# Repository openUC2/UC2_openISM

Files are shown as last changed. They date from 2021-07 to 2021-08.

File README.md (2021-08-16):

<p align="left">

</p>

# openUC2 openISM
---

This is the repository for the openISM project which integrates a laser-scanning module for image-scanning microscopy (ISM) to the UC2-system.

🧾 The manuscript for the openISM and openSIM can be found under the [DOI:10.1101/2021.01.08.425840](https://doi.org/10.1101/2021.01.08.425840)

<p align="center">
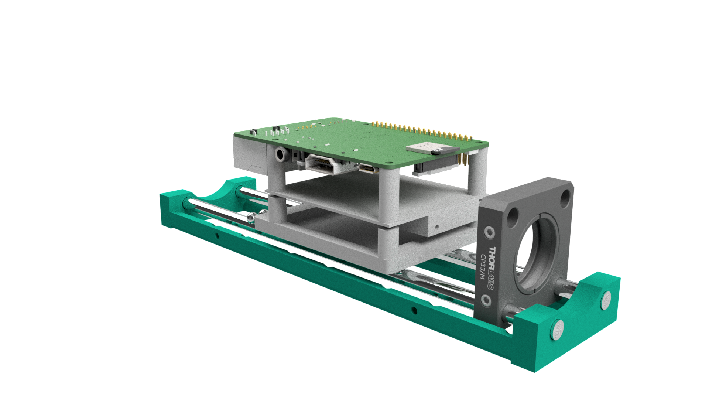
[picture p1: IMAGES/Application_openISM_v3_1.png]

</p>

***Fig 1:*** *This is the ready-to-print module which clicks into the UC2-system. It hosts the Nebra AnyBeam HAT with a Raspberry Pi as a control unit*

This module is based on the work about Image Scanning Microscopy (ISM) by Enderlein et al. [1] and instant Structured Illumination Microscopy (iSIM) by A. York et al. [2]. It uses a low-cost MEMS-based laser-scanning video-project ([Sony CL1A, Tokyo, Japan, 300€](https://www.sony.com.sg/electronics/support/televisions-projectors-projectors/mp-cl1a/specifications); [Anybeam HAT, UK, 200€](https://uk.pi-supply.com/products/nebra-anybeam-hat-laser-projector-for-the-raspberry-pi?lang=de)) to generate a structured illumination for microscopy. We apply a point-wise incoherent lattice/grid-like pattern to increase lateral and axial resolution. The overall gain in resolution is limited, hence more suitable for educational purposes or data generation.  

<p align="center">
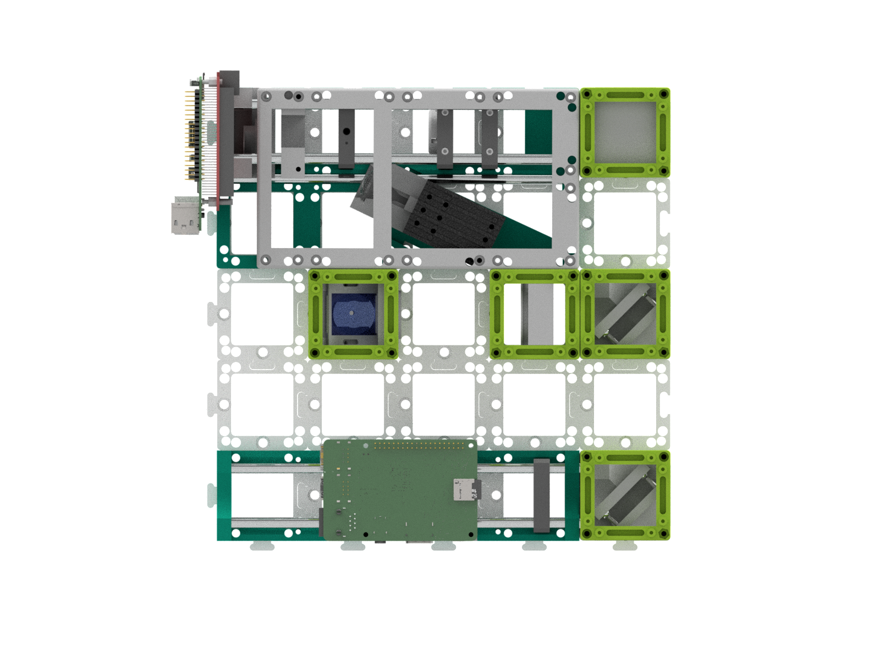
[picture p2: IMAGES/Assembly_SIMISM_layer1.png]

</p>

***Fig 2:*** *This shows the optical assemlby; the laser beam deflected by the scanning mirror is "collimated" and stired by a set of two kinematic mirror mounts before a tube lens (f'=165mm) forms a magnified image in back focal plane (BFP) of the objective lens (not shown) which follows the dichroic mirror*

In recent years portable devices to experience entertainment "on-the-go" like video-projectors or movie screens have found their ways to the consumer market. Many of these produce like portable projectors share the same components as their scientific counterparts (e.g. digital mirror devices, DMD) but for a much lower price since components are mass-produced. Besides wide-field projection system based on LCoS (liquid crystal on silica), LCD or DMD displays, more exotic laser-scanning based systems like the here used Sony MP.CL1A (Japan) enable the creation of laser-scanning microscopes for a very low price (e.g. 300€).

To display a color image on a screen (e.g. wall), a small MEMS (Micro-Electro-Mechanical Systems) scans a set of RGB Blue=450nm, Green}=530, Red = 650, laser-beams over the 2D (e.g. X/Y) plane with a frame-rate of 60fps at a spatial resolution of 1920*720 pixel^2.
This device can easily be integrated in the UC2-system by providing a customized  adapter which makes the device compatible with the 50*5 mm^2 grid. Following the work by Enderlein et al. (ISM) (Muller2010a) and York et al. (iSIM)  (York2012) we displayed an incoherent grid of point sources in the sample plane, which can be used to create a better optical sectioning and improve optical resolution. This is done in a post-processing step, where each 2D image gets divided in a series of tiles of the size of the PSF-extend around one illumination position. Each tile corresponds to a confocal-like measurement, where the information can computationally be confined, when a de-centred detection pinhole is assumed. The resulting signal is placed on a canvas with twice the sampling of the original measurement, which creates an optical super-resolution up to a factor of sqrt(2) (McGregor2015).

Since this device is not meant to be used for scientific instrumentation, there are only limited information available. Also, since the resolution of 1920*720 pixels^2 is not very common, ordinary computers to generate a display on this device where interpolating the images. Connecting the device to a Apple Macbook (USA) at a display-resolution of 720p ensured a one-to-one pixel mapping, where we created a customized Python-script to generate and display the ISM-patterns full-screen. The monochromatic cellphone-camera (Huasei P20, China) was driven using the open-source software FreeDCam (Fuchs2018), where the exposure time t=1/60s matches the frame-rate of the laser-scanning projector in order to reduce bouncing effects of both refresh-rates.

<p align="center">
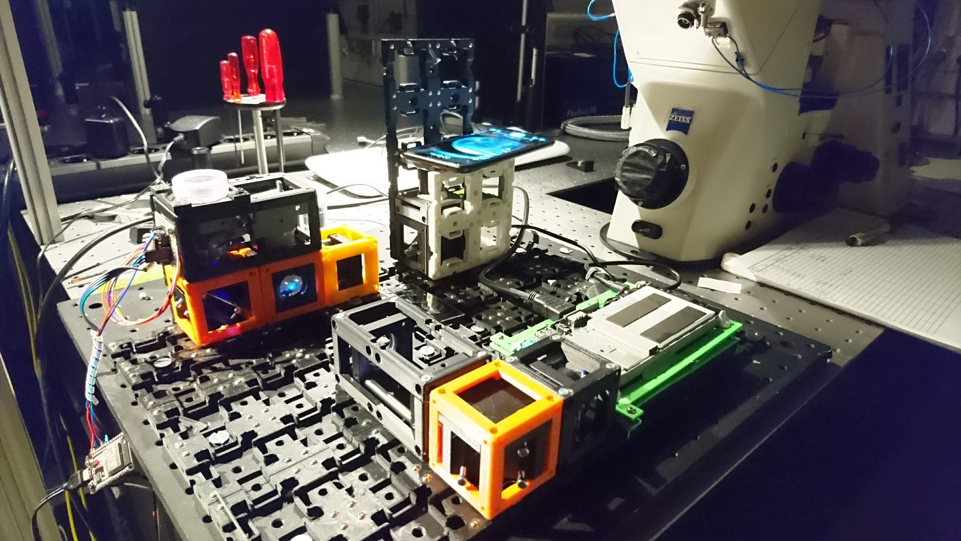
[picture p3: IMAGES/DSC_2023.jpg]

</p>

***Fig 3:*** *The full system based on the modular cubes. This variant is based on a cellphone camera as the detection system. Also instead of the AnyBeam MEMS projector, we use the SONY device*

***Features:***
- Increased optical sectioning and higher resolution
- Very low cost:  ~300€
- Easy to align
- Open-Source
- Three wavelengths

## Optical System

<p align="center">
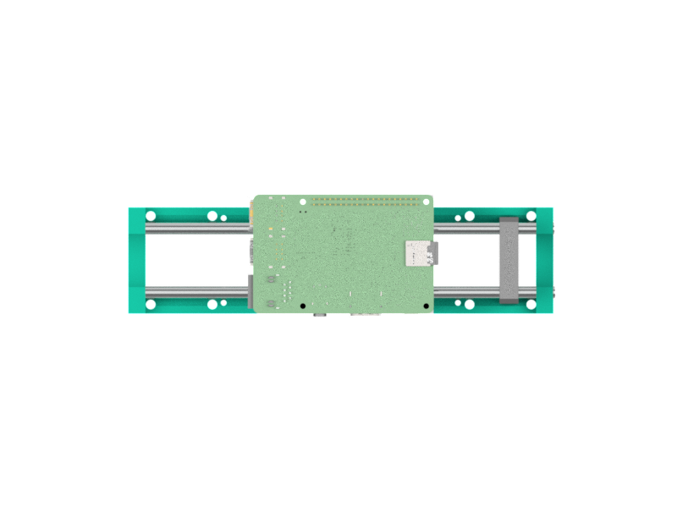
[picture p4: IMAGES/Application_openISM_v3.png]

</p>

## Optical Setup

**NEED TO BE UPDATED**

The optical setup shown in Fig. 1 is straight-forward. The resonating MEMS in the projector needs to be imaged into the BFP of the microscope objective lens. In order to get high-resolution images, the BFP is over-filled by the mirror ideally. We assumed a diameter of the aluminium mirror of d_{mirror}=1.5mm and a diameter of the BFP of around d_{BFP}=5.5mm which requires a telescope, created by a lens f'_1=30mm and a following tube-lens f'_2=180mm. The low-cost infinity-corrected microscope objective (Optika, 20x, NA=0.4,  N-plan, [here](https://www.optik-pro.de/fuer-mikroskope/optika-objektiv-20x-0-40-infinity-n-plan-pol-b-383pol-m-146p/p,56893#tab_bar_1_select) was put in a motor-driven Z-stage to allow focussing the objective relative to the sample. A set of different dichroic-mirror cubes with suitable filters allows the switching between different fluorophores and excitation wave-lengths.

# Table of Content
* **[Software](#-software)**
* **[Hardware](#-hardware)**
* **[Bill of materials](#-bill-of-materials)**
* **[Electronics](#-electronics)**
* **[Results](#-results)**

# Software
### Install the Anybeam Nebra with the Raspberry Pi

Please follow the steps mentioned on the [AnyBeam HAT github page](https://github.com/NebraLtd/AnyBeam/).

Open the file ```/boot/config.txt``` and add the following lines:

```
# Additional overlays and parameters are documented /boot/overlays/README
dtoverlay=dpi24
overscan_left=0
overscan_right=0
overscan_top=0
overscan_bottom=0
framebuffer_width=1280
framebuffer_height=720
enable_dpi_lcd=1
display_default_lcd=1
dpi_group=2
dpi_mode=85
dpi_output_format=0x070027
```

# Hardware

Below we describe how the device can be build and assembled in order to replicate the whole system as shown in the rendering above. One needs additional parts that can be found in the core [openUC2 repository](https://github.com/bionanoimaging/UC2-GIT).

## Electronics
### Having a look into the MEMS-based laser projector (old version with Sony)

<p align="center">
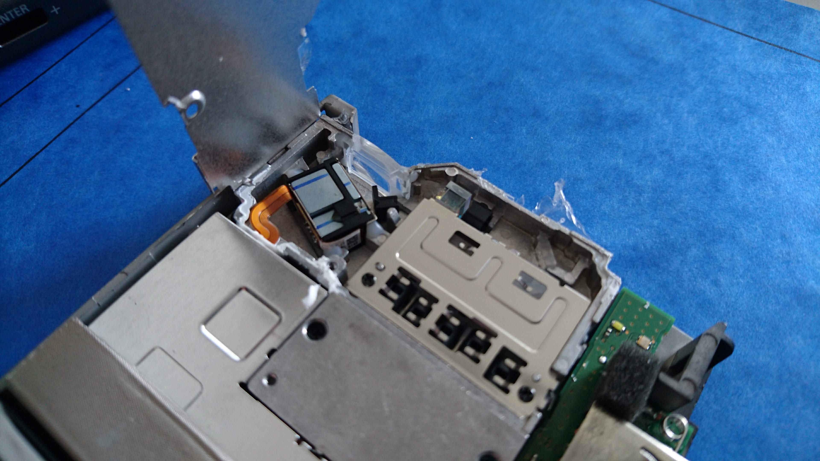
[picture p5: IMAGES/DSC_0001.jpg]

</p>

***Fig 1:*** *The assembly faeatures three laser wavelengths fused with a complicated assembly of optical parts to remove speckles*

<p align="center">
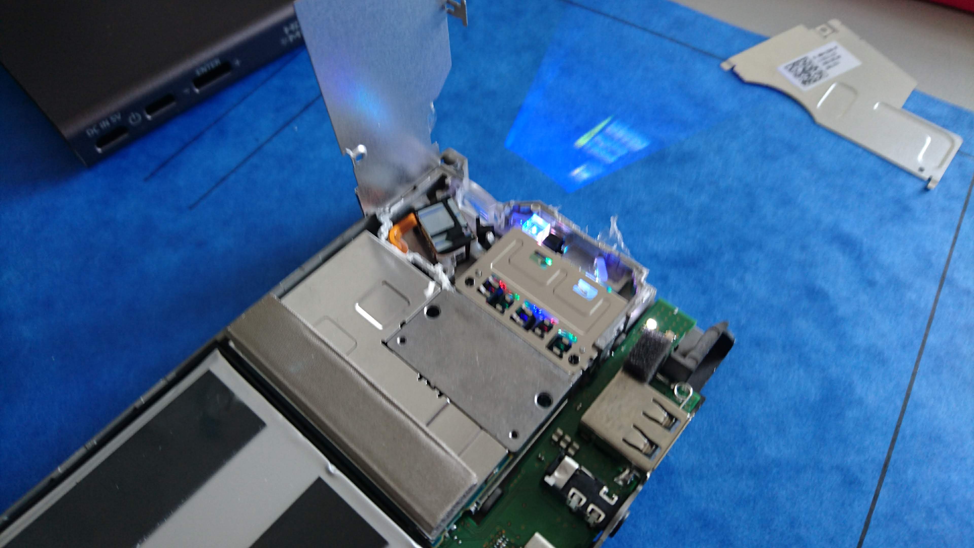
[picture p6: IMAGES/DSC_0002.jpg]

</p>

***Fig 2:*** *Funnily, the polarization beamsplitter from a bluray drive fits in there to enable any kind of descanning arrangement*

<p align="center">
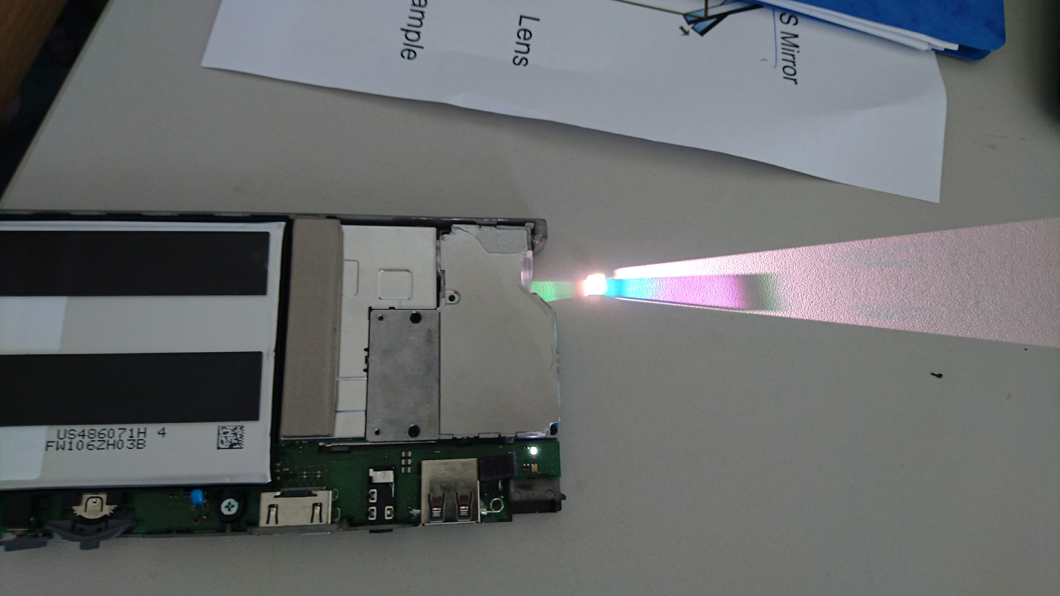
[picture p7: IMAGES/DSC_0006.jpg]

</p>

***Fig 3:*** *Beam coming out of the projector*

## Bill of material

Below you will find all components necessary to build this device

### 3D printing files

All these files need to be printed. We used a Prusa i3 MK3 using PLA Prusament (Galaxy Black) at layer height x.x mm and infill xx%.

Parts to print:

* 1× [openISM AnyBeam Mount](./CAD/20_Cube_insert_openISM_AnyBeamMount.stl)
* 1× [Cube insert openISM vase v3](./CAD/20_Cube_insert_openISM_vase_v3.stl)

### Additional parts
This is used in the current version of the setup

<strong>(This is for the Anybeam, since the Sony projector seems to be discontinued)</strong>

|  Type | Details  |  Price | Link  |
|---|---|---|---|
| MEMS | Nebra AnyBeam HAT |  200 € | [Pi Supply](https://uk.pi-supply.com/products/nebra-anybeam-hat-laser-projector-for-the-raspberry-pi?lang=de)  |
| Raspberry Pi | Raspi+SD-Card+Case+Powersupply(for DMD+Raspi, 5V, >=3A!) |  70 € | [Reichelt](https://www.reichelt.de/raspberry-pi-4-b-4x-1-5-ghz-1-gb-ram-wlan-bt-rasp-pi-4-b-1gb-p259874.html?PROVID=2788&gclid=Cj0KCQiAz53vBRCpARIsAPPsz8X9hCOt9yVVB_WqLCmKSs2e-KuThVnrMEtl2TRbAUTqtVoNZU3zM3YaAg2ZEALw_wcB&&r=1)  |
| "Scan" lens | 1x Achromatic 1 inch Lens, f=30mm |  82 € | [Thorlabs](https://www.thorlabs.com/thorproduct.cfm?partnumber=AC254-030-A)  |
| 5mm ball magnets  | 8x Neodym Ball Magnets |  5 € | [Various]()  |
| 6mm Rods | 20mm Rods (ferromagnetic/galvanized), 6mm diameter   |  40 € | [Thorlabs, Edmund Optics ?]()  |
| M3 Screws | Various |  1 € | [Various]()  |

### Design files
The original design files are in the [INVENTOR](./INVENTOR) folder. *FOR ANOTHER FORMAT, GET YOUR OWN FOLDER.*

### Problems with the Nebra Anybeam

The pattern of the Nebra Anybeam HAT seems to fluctuate temporally. We believe this is due to the scanning scheme of the MEMS.
Read more [here](https://github.com/NebraLtd/AnyBeam/issues/14).

<p align="center">

</p>

***Fig 1:*** *One can observe a gitter which moves temporally*

<p align="center">

</p>

***Fig 2:*** *The three different wavelenghts are not in-line*

<p align="center">
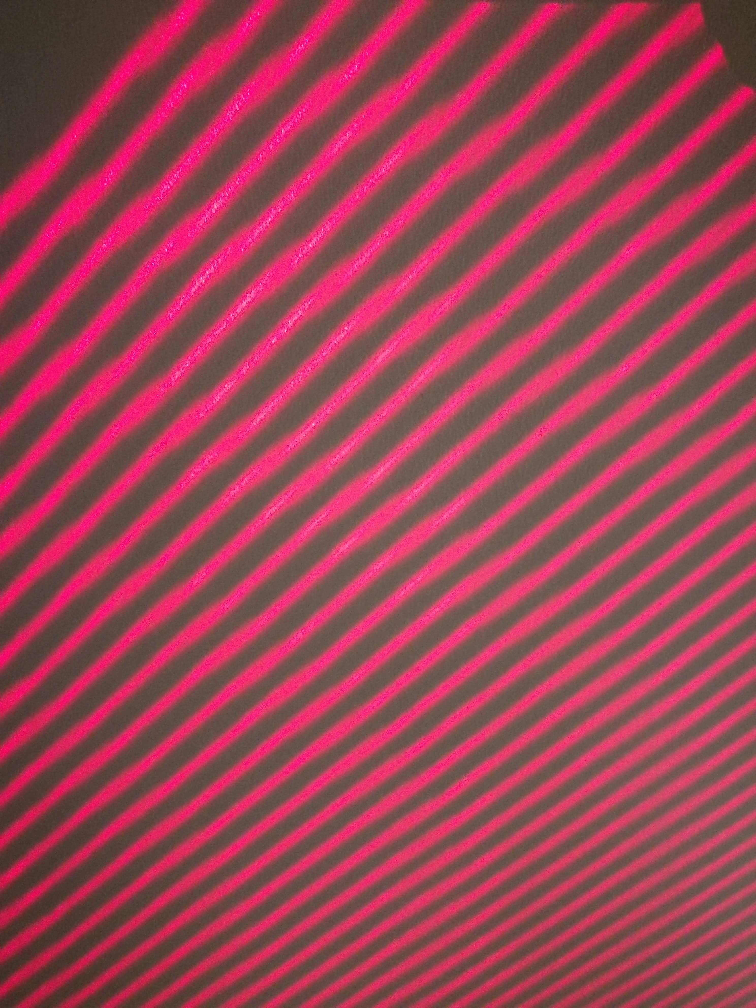
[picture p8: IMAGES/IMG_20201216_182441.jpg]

</p>

***Fig 3:*** *Inhomogenities due to bouncning of the pixels*

## Showcase
This is just one frame of some fluorescent pollen grains:
<p align="center">
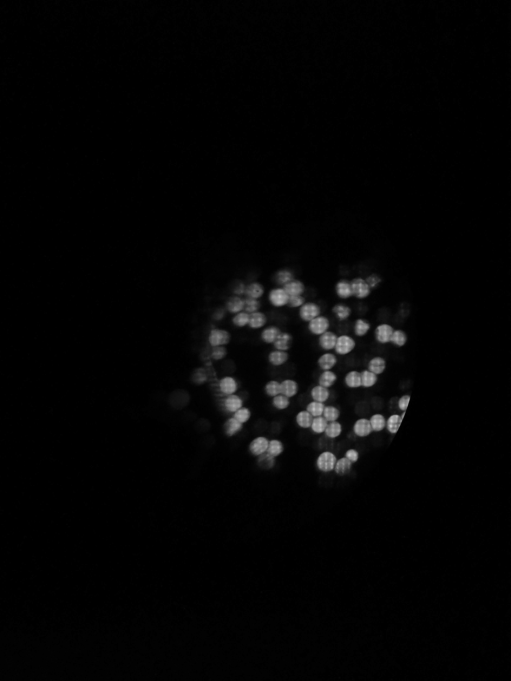
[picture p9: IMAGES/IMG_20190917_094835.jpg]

</p>

<p align="center">
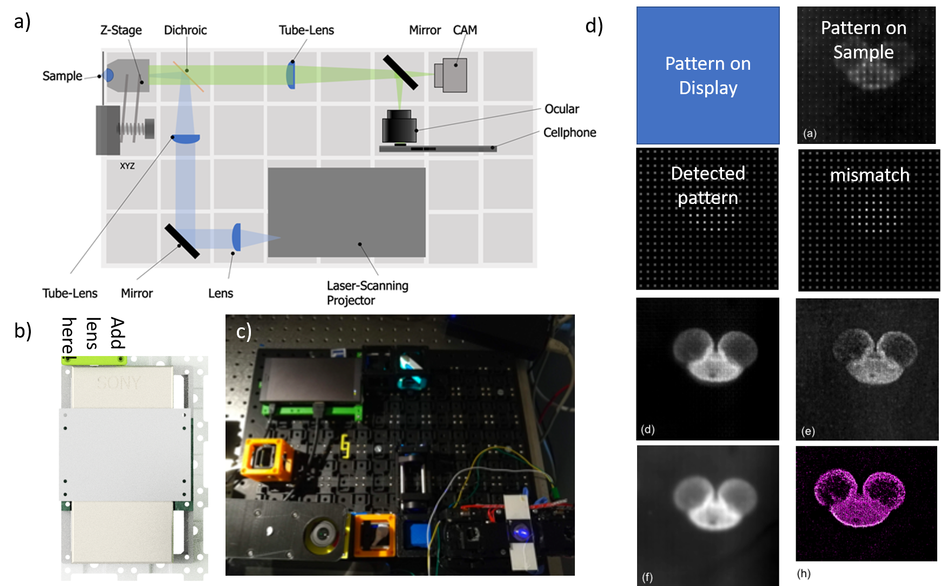
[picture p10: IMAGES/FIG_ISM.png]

</p>

## Get Involved

This project is open so that anyone can get involved. You don't even have to learn CAD designing or programming. Find ways you can contribute in  [CONTRIBUTING](https://github.com/openUC2/UC2-GIT/blob/master/CONTRIBUTING.md)

## License and Collaboration

This project is open-source and is released under the CERN open hardware license. Our aim is to make the kits commercially available.
We encourage everyone who is using our Toolbox to share their results and ideas, so that the Toolbox keeps improving. It should serve as a easy-to-use and easy-to-access general purpose building block solution for the area of STEAM education. All the design files are generally for free, but we would like to hear from you how is it going.

You're free to fork the project and enhance it. If you have any suggestions to improve it or add any additional functions make a pull-request or file an issue.

Please find the type of licenses [here](https://github.com/openUC2/UC2-GIT/blob/master/License.md)

REMARK: All files have been designed using Autodesk Inventor 2019 (EDUCATION)

## Collaborating
If you find this project useful, please like this repository, follow us on Twitter and cite the webpage! :-)

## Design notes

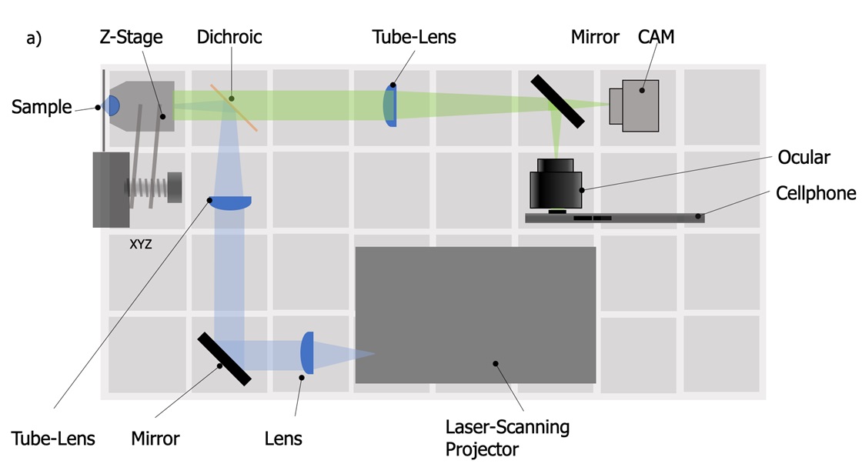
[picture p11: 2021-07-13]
IMAGES/ISM.jpg

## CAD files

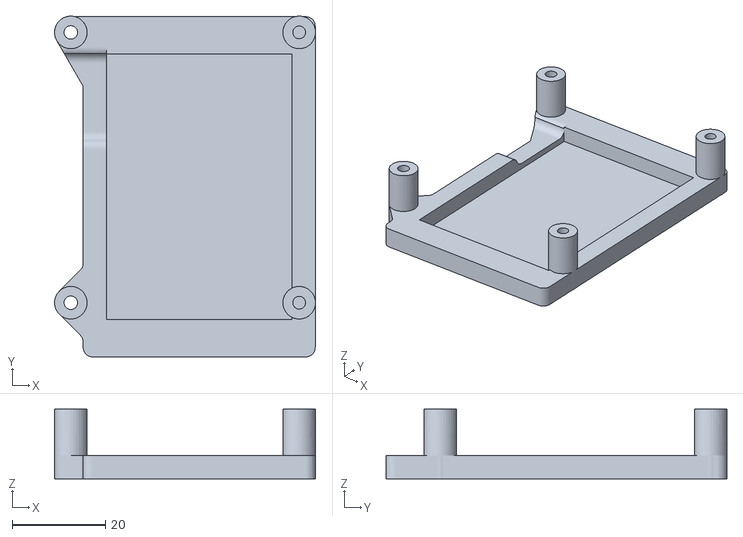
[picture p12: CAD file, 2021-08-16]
CAD/20_Cube_insert_openISM_AnyBeamMount.stl
56.0 x 73.1 x 15.0

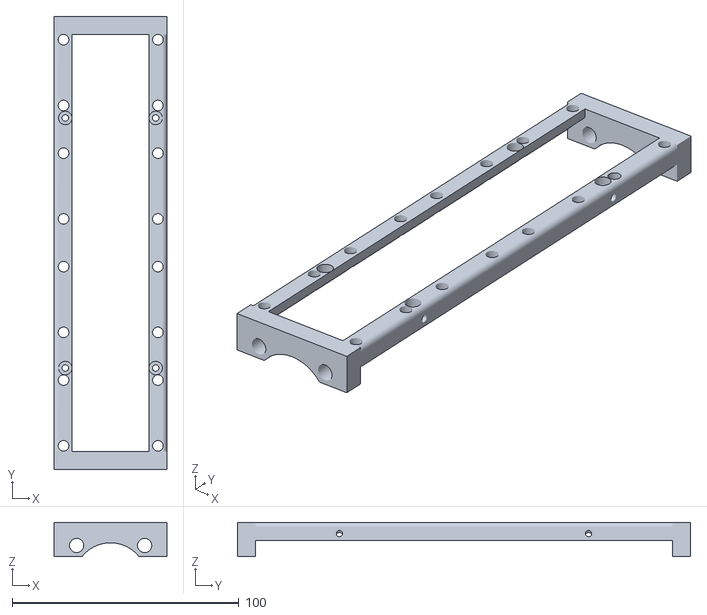
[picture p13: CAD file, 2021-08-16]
CAD/20_Cube_insert_openISM_vase_v3.stl
49.8 x 199.8 x 15.0

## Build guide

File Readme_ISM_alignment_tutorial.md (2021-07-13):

# ISM alignment tutorial

This tutorial is aming to align the openISM module to the microscope. The required components and setup steps are similar to the openSIM module which is in the Github repository.

  - openISM module
  - optical components
  - UC2 cubes and inserts
  - target sample
  - magical hand
  
## Introduction of the openISM module

In the openISM module, the illumination source is a commercially available laser video projector (Sony/Anybeam HAT). Both of them have integrated different colored laser diodes and the desired image is displayed with the help of a MEMS mirror. In this project, we have built a openSIM/ISM setup, which the imaging and sample modules of the setup are shared. The illumination of the openISM module is shown in Fig. 1. 
<p align="center">
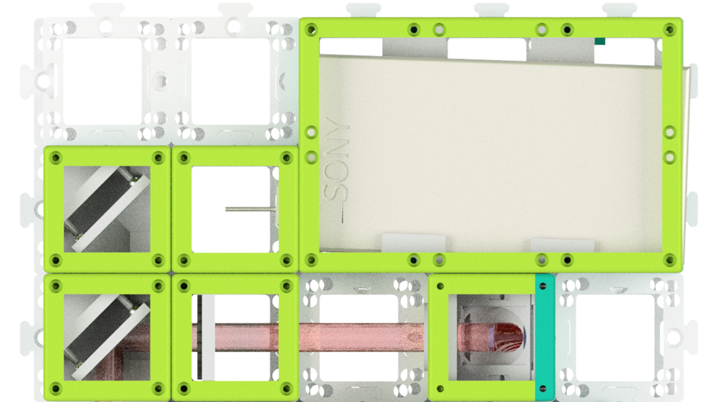
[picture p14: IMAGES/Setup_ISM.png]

</p>

***Fig. 1*** *The openISM illumination module based on our UC2 CAD design. Comparing to the openSIM module, the ISM part is relative simply thanks to the projector, which has integrated laser diodes and MEMS mirror. The laser beam is directed twice with the help of two mirrors and focus on the back focal plane of the objective.*

The spectra of both projectors are illustrated in Fig. 2
<p align="center">
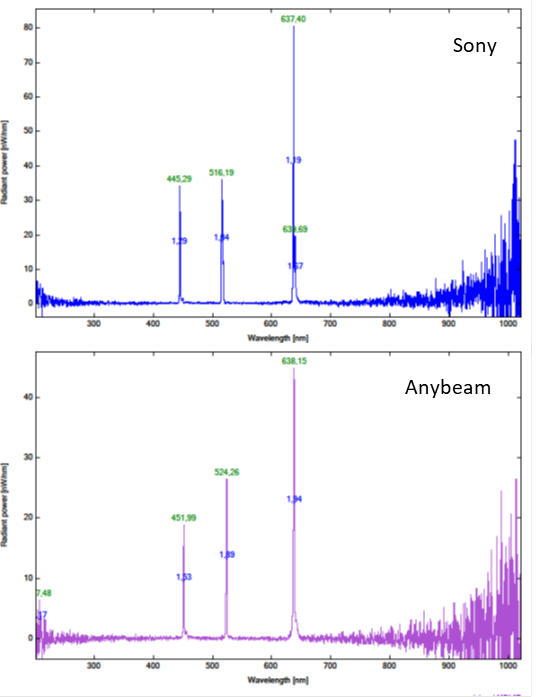
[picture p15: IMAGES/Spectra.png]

</p>

***Fig. 2*** *Spectra of Sony/Anybeam laser projector.Both projectors used the laser diodes which have similar spectra. They can used to excite fluorescent, such as GFP, mCherry and Alexa Flour 647, with the correct filter set.*

## Alignmen of the telescope
After collimate the beam with first lens, the beam is directed by two mirrors to the second 165 mm lens. After the second lens, the beam should refocus at the back focal plane (BFP) of the objective and reimage the MEMS mirror. Due to the effct of the freeform lens integrated in the sony projector, the collimated beam from sony shaped a round shape with some unexpected external strucutres.

<p align="center">
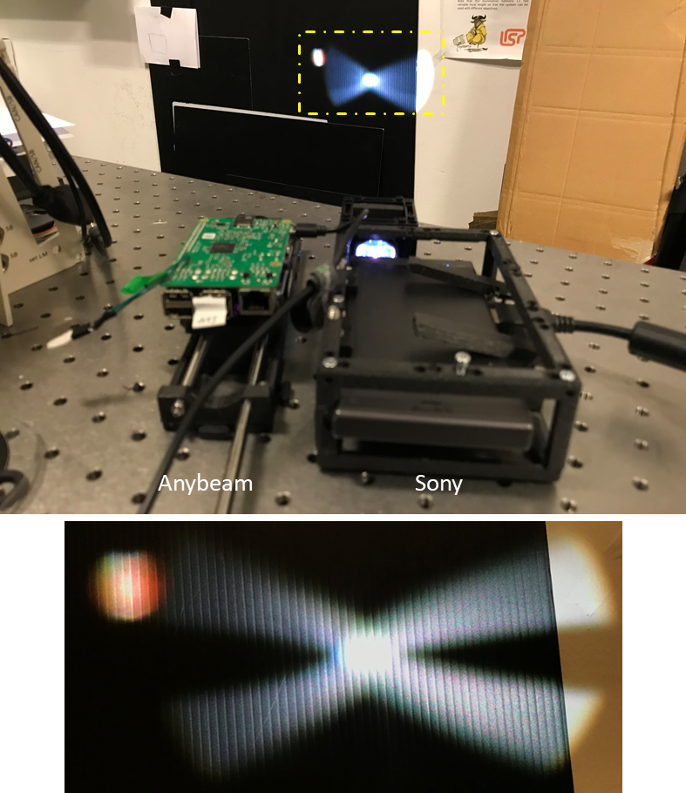
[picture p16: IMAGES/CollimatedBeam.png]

</p>

***Fig. 3*** *The laser beam come from both projectors is collimated by the first lens of the telescope. The beam should keep the same size irrelevantly to the distance. The lower image shows the detail of the beam at the wall. The beam shape from the Sony projector is not only a round spot due to the freeform lens in front of the MEMS mirror.*

## Alignment of the system
When the setup is in general once adjusted, place the objective cube with z-stage on it. We updated a new [linear z-stage](https://en.wikipedia.org/wiki/Update) which is compatible with injection moulded cube. Put a sample on the stage and turn on the projector to display some image, we should observe at least some part of the image on the camera, when not, try to center the image at the position of the objective. Slightly adjust the position of the image pattern with rotate the adjusting screws of the kinetic mirrors. A well-aligned openISM module should capture the point array pattern similar to this:

<p align="center">
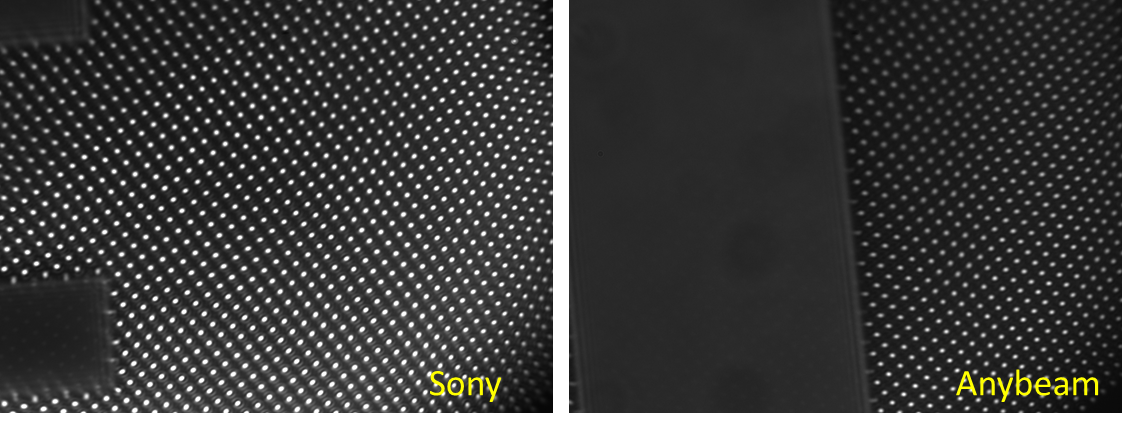
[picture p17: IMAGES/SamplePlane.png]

</p>

***Fig. 4*** *After alignment, the image at the sample plane should be as shown here. The point array image is illuminated on a negative USAF target, with good aglinment, the point array should focus at the surface of the target with sharp pattern.*

Now the setup is ready to use and try to lighten some fluorescence samples!
